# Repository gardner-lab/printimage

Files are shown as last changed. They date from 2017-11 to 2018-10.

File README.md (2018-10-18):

# Requirements

- [ScanImage](http://scanimage.vidriotechnologies.com/)  by Vidrio Technologies.
  - Version ≥5.2.4 ([Requirements](http://scanimage.vidriotechnologies.com/display/SIH/ScanImage+Installation+Instructions))
  - Other versions, including the nonfree versions, may also work, but are untested.
  - PrintImage requires that these pieces of hardware be configured in ScanImage:
    - Resonant scanner
    - Fast Z piezo stage
    - Pockels cell controlled by a fast analogue output card
    - Pockels power calibration hardware (e.g. a photodiode)
    - For stitched printing: an XYZ stage with around 0.1% linear error
- Mesh Voxelisation by Adam H. Aitkenhead: [Matlab File Exchange 27390](https://www.mathworks.com/matlabcentral/fileexchange/27390-mesh-voxelisation)
- STL File Reader by Eric Johnson: [Matlab File Exchange 22409](https://www.mathworks.com/matlabcentral/fileexchange/22409-stl-file-reader)
- Significant Figures by Teck Por Lim: [Matlab File Exchange 10669](https://www.mathworks.com/matlabcentral/fileexchange/10669-significant-figures)

# Installation

- Install ScanImage in the MATLAB path
- Run ScanImage and set up your hardware
- Calibrate hardware
  - Lens safe working depth
  - Lens FOV
  - Resonant scanner degrees per volt
  - Galvo degrees per volt
  - Slow XY or XYZ stage accuracy
  - Fast Z stage accuracy
- Patch the ScanImage code. In a shell, go to your ScanImage base directory, and run something like `git apply ../printimage/scanimage-integration/patches/scanimage-5.3.1.patch --whitespace=fix` (here I've assumed that scanimage and printimage are subdirectories of a common parent). If you don't see your favourite ScanImage version here, look at the patch: it's dead simple!
  - [For ScanImage 5.2.4](scanimage_integration/patches/scanimage-5.2.4.patch)
  - [For ScanImage 5.3](scanimage_integration/patches/scanimage-5.3.patch)
  - [For ScanImage 5.3.1](scanimage_integration/patches/scanimage-5.3.1.patch)
  - [For ScanImage 5.4](scanimage_integration/patches/scanimage-5.4.patch)
- Install PrintImage and the above packages in the MATLAB path
- Modify the appropriate PrintImage default parameters (this will be in a configuration file eventually)

# Calibration

Size Calibration is done through parameters in ScanImage's `Machine_Data_File.m`, not through PrintImage. This is because we figure you'll want your microscope calibrated properly whether or not you're printing anything today.

I will refer to the axis over which the resonant scanner scans as X. The galvo scans over Y. The "fast Z" stage, perpendicular to the focal plane, is (surprise!) Z.

Unsurprisingly, you will want to set zoom to 1, using either ScanImage's interface or `hSI.hRoiManager.scanZoomFactor = 1`

For X and Y, three parameters affect two degrees of freedom. I think there's a correct way to do this, but I'll describe the kludge.

## X and Y (field of view)

### Background

ScanImage mainains its idea of the lens's field of view in a variable called `hSI.hRoiManager.imagingFovUm`. This is a matrix giving the corner positions of the FOV. I've assumed that this is square and centered around 0, so if it's not, my code will be buggy! But here's one way to read ScanImage's idea of the FOV in X and Y:

        fov = hSI.hRoiManager.imagingFovUm
        [fov(3,1) - fov(1,1)      fov(3,2) - fov(1,2)]

### Parameters in `Machine_Data_File.m`

- `objectiveResolution` controls X and Y FOV together
- `rScanVoltsPerOpticalDegree` controls the magnitude of the voltage signal to the resonant scanner (X)
- `galvoVoltsPerOpticalDegreeY` controls the magnitude of the voltage signal to the galvo (Y)

### Setting the values

You'll need a way to measure the actual FOV. This can be done by imaging something of known size, or by printing something and then measuring it on a calibrated device. For this purpose we have calibration rulers. <em>FIXME Add links to our calibration rulers and the paper's instructions.</em>

This accomplished, compute your error in X and Y, and just multiply some combination of those numbers to scale the image. It is likely that the numbers have nominal values (e.g. for our hardware, in theory `galvoVoltsPerOpticalDegreeY = 1`), so maybe try not to stray too far from those values, or keep one of them at the nominal value or something. We've found that one iteration of this procedure can get us to within 1% or so.

### Scan phase

If the size of objects appears different on the left vs. right sides of the display (e.g. if you print or image a grid, and scrolling left-right changes the apparent grid size), you may need to adjust the scan phase. It's `hSI.hScan2D.linePhase`, available in the "Scan Phase" box in ScanImage's CONFIGURATION window. I haven't had much luck with "Auto Adjust".

Note that since this is not available in `Machine_Data_File.m`, I set it by hand in `printimage.m`. This will be moved to a printimage config file soon... For now, change the value until it looks right, and then modify `hSI.hScan2D.linePhase` in `printimage.m`.

## Z scale (adjusting the FastZ actuator)

### Background

ScanImage allows you to specify certain known models of FastZ stage. From `Machine_Data_File.m`:

        actuators(1).controllerType = 'thorlabs.pfm450';           % If supplied, one of {'pi.e665', 'pi.e816', 'npoint.lc40x', 'analog'}.

We have a ThorLabs pfm450, which ScanImage <em>should</em> know how to talk to. However, ours was not moving quite as far as ScanImage expected. In order to correct that, I modified some variables.

Also, note that it is essential to run at least our FastZ controller in closed-loop mode!

### Measuring the error

The procedure is generally the same as for X and Y: either print something of ostensible size and measure it, or image something of known size. For this we provide a vertical pyramid ruler. <em>FIXME Link to it!</em>

### Setting the values

If you need to adjust the scaling, you must <em>not</em> tell ScanImage what kind of FastZ controller you have, so it will actually use your adjusted values rather than its own. Just tell it you're using an analog controller:

        actuators(1).controllerType = 'analog';          % If supplied, one of {'thorlabs.pfm450', 'pi.e665', 'pi.e816', 'npoint.lc40x', 'analog'}.

Now, adjust the VoltsPerMicron values according to your measurements:

        actuators(1).commandVoltsPerMicron = (10/450)/1.1;    % Conversion factor for desired command position in um to output voltage

The maximum voltage is 10 (specified in the manual, transcribed to `actuators(1).maxCommandVolts`; likewise the 450 and other constants (see below).

<em>The "/1.1" is the important part--it compensates for the 10% error that we measured.</em>

        actuators(1).commandVoltsOffset = [];        % Offset in volts for desired command position in um to output voltage
        actuators(1).sensorVoltsPerMicron = (10/450)/1.1;     % Conversion factor from sensor signal voltage to actuator position in um. Leave empty for automatic calibration

Same thing here--the sensor was off by the same amount. That led us to double-check our measurements (looks like two independent (?) systems were in agreement), but the printed parts really were the wrong size, measured on an SEM and via our slow Z stage (Sutter MOM, which is notoriously inaccurate but which in this case agreed with the SEM, as well as with itself at different locations in its range). So that can happen, I guess. Photoresist shrinkage? Anyway, our parts are the right size now.

        actuators(1).sensorVoltsOffset = -0.12;        % Sensor signal voltage offset. Leave empty for automatic calibration
        actuators(1).maxCommandVolts = 10;          % Maximum allowable voltage command
        actuators(1).maxCommandPosn = 450;           % Maximum allowable position command in microns
        actuators(1).minCommandVolts = 0;          % Minimum allowable voltage command
        actuators(1).minCommandPosn = 0;           % Minimum allowable position command in microns

## Leveling (with a hexapod)

### Background:

Desiderata:
- We want the slide (or printable medium) to be parallel with the optical plane.
- We want moves to track the optical plane.

Now imagine that your printable medium is a piece of something (e.g. an electrode in need of a cuff) loosely taped onto a slide. It may not be parallel to, well, anything. First step is to tilt the medium into alignment with the optical plane. Second step is to align the movement coordinate system.

### Tilting

Start a "focus", and add a bullseye. Focus on the substrate, and then bring the lens up just far enough to see a hint of fluorescence beginning to show. Use the hexapod's angle controls to put that hint of fluorescence in the middle of the FOV (using the bullseye). It will probably be necessary to tilt the object and then re-focus on the hint-of-fluorescence, tilt some more, re-focus again, etc.

### Leveling

Again focus on the substrate and then bring the lens up just far enough to see a hint of fluorescence, as above. Run a "brightness test" and look at the results (FIXME `falloff_slide.m` right now, but that's not ready for primetime). The goal will be to set the leveling coordinate system so that the (possibly tilted, but optically aligned) substrate moves along the optical XY plane. This is controlled by 
  `STL.motors.hex.leveling = [ X Y Z U V W ];`
Set it in `printimage_config.m`, and adjust as needed. For example, on our printer:
- If brightness increases as X increases, increase V (pos 5)
- If brightness increases as Y increases, increase U (pos 4)
Your printer may differ.

My favourite workflow: edit the values in `printimage_config.m`, copy and paste the definition into the MATLAB commandline, and run `hexapod_set_leveling()`, which will store the values in the hexapod. Run another brightness test and repeat until the brightness traces don't change too much over XY movement (I can usually get them down to about 10% variation, depending on how close I am to the substrate).

The sixth value of `STL.motors.hex.leveling` controls the alignment of stitched parts. Print something stitched and adjust W in order to align the hexapod's XY motion with the resonant-galvo axis.

### Saving the tilt

One more parameter should be saved in `printimage_config.m`:
  `STL.motors.hex.slide_level = [ 0 0 0 0.255 -0.09 0 ];`
These numbers are the tilt offsets from the tilt calibration process, above, but they must be read _after_ the leveling coordinate system is correctly defined and tuned.

## Vignetting compensation

### Background

This began as an effort to model the falloff due to optical vignetting. The theoretical model of cos(theta)^4 seemed to fit pretty well, but couldn't be justified for a near-field laser (i.e. working less than a few kilometres from the laser source). And then I reasoned that since all models are wrong, it might be better to do something free-form. Hence the adaptive power compensation.

### THINGS I NEED TO FIX

- This requires a stitching stage with good precision, and currently actually requires the Physik-Instrumente hexapod controller! Sorry... I'll see about fixing that, or helping someone with other hardware to write a patch.
- I need to figure out at what size and zoom to print the test object!

### How?

Zero: Set your desired print zoom level...? Still working on this.

First, focus within the IP-Dip (yielding a fluorescent image that appears approximately Gaussian). Use `Calibrate / Save baseline image` to save the default brightness at the camera.

Second, find the substrate: follow the instructions regarding "Finding 0" in "Printing" (below in this document), and use the `Calibrate / Calibrate vignetting compensation` menu item to begin. This will:
- Load and print a "cube" (actually a rectangular prism) of the size defined at the top of `calibrate_vignetting_slide.m`.
- Servo the stitching stage over the printed cube near its surface (currently `height - 2` um) and measure the brightness at lots of points
- Fit a curve to the measured brightnesses
All future prints will use this curve to adjust the power in real time as objects print. If the curve isn't producing good results, you may do the same thing again (start with "Finding 0" again), which will print another cube using the curve you just generated, measure output, and create a new fit, _which will be stacked on top of the old one._ In this way, you may iterate until you get good results (I've only tried up to 5 iterations; there is no software limit but I have found that I get diminishing returns or even degradation of results after about 2. YMMV).

To start from scratch, use the `Calibrate / Clear vignetting compensation` menu item. You may then start again. Feel free to add your own calibration procedure! They're applied in `printimage_modify_beam.m`.

# Printing

## Preparing the sample

- Undeveloped IP-Dip is _extremely_ toxic. Use gloves, and treat all spills, wipes, etc., as biohazard waste.
- Place a drop of IP-Dip on the substrate.
  - We use a syringe or a stirring rod to place the IP-Dip.
  - For a test substrate, we use a microscope slide cover slip suspended by its ends. This ensures that if the lens is lowered too far, the cover slip will break before anything expensive.

## Interacting with the substrate

The working distance of the lens is important, as you do not want the lens to touch anything solid! Our lens has a 380-um working distance, which has the following implications:
- If we are focused on the surface of the substrate we can move down another 380 microns before something breaks.
  - If we have just printed something 200 um high, we can scroll down 180 um before the lens hits the thing we just printed.
- If we are imaging at substrate+10 um and moving the XY stage, anything over 390 um (previously printed, or slide holders, etc) can potentially hit the lens.

### Finding 0 (where the substrate meets the IP-Dip)

- Lower the lens until it touches the IP-Dip.
- Set ScanImage's zoom level to 1.
- Set ScanImage's power level somewhere too low to cause polymerisation. This will take experience, but start at 5%. On our equipment, at zoom level 1, polymerisation does not happen below around 40%, so we image at 10% or so.
- Press the ScanImage "FOCUS" button to begin obtaining images.
  - ScanImage's view window should glow, and you will probably see some vignetting at zoom=1.
- IP-Dip fluoresces at the print wavelength (780 nm), and glass does not. As long as the lens is focusing in the IP-Dip, the microscope will show an image. Lower the lens until the whole FOV turns dark, indicating that the lens is now focused on the substrate. Lowering another micron or 3 ensures good bonding.

### Printing in a specific location (e.g. on a nonuniform object attached to the substrate)
- Align according to your best guess.
- Find an appropriate lens depth (Z).
- Search outward from there using the "Search" button until the object you want to print on appears in the image.
- If you must manually rotate the sample, it is helpful to tell PrintImage about the axis of rotation:
  - Find the centre of your rotation stage by imaging something (possibly something you just printed) and rotating the stage, servoing until the centre of rotation is in the centre of the ScanImage imaging window.
  - Press the PrintImage "Set rotation centre" button.
    - You may also want to change the PrintImage parameter STL.logistics.rotation_centre to match this.
  - From now on, if you manually rotate the stage, you can have PrintImage track the location of the object by entering the angle of rotation in the "Track rotation" box.
- The "Print preview" button will paint the current preview slice (PrintImage's rightmost figure) where PrintImage will print it. You can then move the item under the image to align it.
  - But it's not quite accurate: it shows where PrintImage will turn up the power to the Pockels, but does not take into account any delays in the latter's response.

## Power calibration

PrintImage's "Power Test" button will print a bunch of rectangular prisms at various power settings, which can be seen in ScanImage's "Power Box Settings" window, available through the "POWER CONTROLS" window.
- Unfortunately there is a nonlinear relationship between zoom level, Z step size, and polymerisation power required. If those parameters change, you should re-run the power test at that level.
- Set the "Print Power" level to something that polymerises but doesn't bubble.

## Understage zeroing

### Aligning a rotation stage with the microscope stage

Print something (e.g. a power test pattern). Use the rotation slider to rotate the stage, and see if it rotates about the centre of the screen (the "bullseye" can be used to facilitate this). Move the microscope stage toward what looks like the centre of rotation. Repeat until the image rotates about the centre of the field. This is the alignment point. You may add "STL.motors.mom.understage_centre = [12655 10857 16890];" to  your printimage_config, reading those numbers off the microscope stage's location (microns).

### Leveling a hexapod

Find the substrate, and then pull the lens just a little bit away from it so you can just see some light in the image centre. Scroll up and down on Y while adjusting the hexapod's X rotation control such that scrolling on Y doesn't affect the spot's brightness (closeness to substrate). Vice versa for X-Y.

For Z, print something that involves stitching, such as a linearity test. Scrolling back and forth with the microscope's stage should produce motion parallel with the line of dots that the stitching procedure produced.

The final numbers can be added to printimage_config; e.g., "STL.motors.hex.leveling = [0 0 0 0.9 -0.1 -1.1];"

## Controlling print dimensions

- Your system probably has the worst resolution along the resonant scanner's axis, which we call X. If the object to be printed has finer features along one dimension than another, use PrintImage's dimension buttons to choose to place the coarser features along X
- Objects are printed in slices from Z=0 to higher Z. Slices that print later must attach to slices that print earlier. The Z axis should have no overhangs.
  - Because PrintImage is so fast, we have noticed that some overhangs are okay: the overhanging part may not have time to drift away. But this is untested: do not rely on it! Rather, choose Z so that there are no overhangs.

## Controlling print resolution

X and Y resolutions are functions of various things (position on the X axis, zoom level, hardware...), and you have limited control over them. Z is easiest.

- X "resolution" is always determined by the speed of the analogue output card controlling your Pockels cell. It will always be as high as it can be. There's no single number for this--voxels are smaller near the edges of the FOV than in the middle where the resonant scanner moves the beam faster. Sorry.
- Y resolution is controlled by the number of Y scan lines: ScanImage's `Lines / Frame` parameter in the CONFIGURATION window, also available at the command line through `hSI.hRoiManager.linesPerFrame`. It is always a power of two, so the choice of actual resolutions is somewhat limited. Resolution is the FOV / number of scan lines. Useful resolutions are determined by your photoresist, optics, etc.
- Z resolution is agnostic to zoom level, and it's measured in real units. Woot! Please control this through PrintImage's variable `STL.print.zstep`, which is in microns, and it will instruct ScanImage correctly <em>assuming ScanImage moves your FastZ stage in the same direction as mine with the same voltage change. You may need to change the sign and do a little minor debugging.</em> (Internally, PrintImage controls ScanImage's internal variable `Steps/Slice` in the FAST Z CONTROLS window (`hSI.hStackManager.stackZStepSize`).) One version of the PrintImage interface gives you direct control over that, but if you don't see it, then you have to modify the variable in `printimage.m`.

## Controlling print size

Because STL files are dimensionless, you have to choose the size of the object.

### Stitching

If the object to be printed exceeds any of the dimensions allowed by your hardware, PrintImage will break it into parts and print them in sequence using your XYZ stage.
- Z and safe-working-depth warning!

# After printing

## Inspecting the print

## Resetting the Z position

## Developing the print

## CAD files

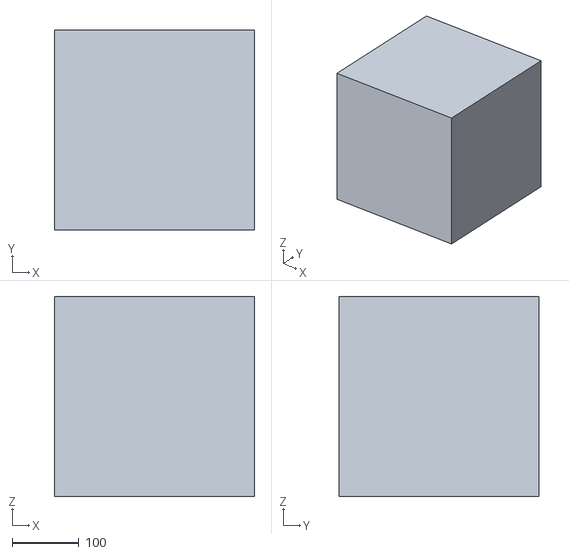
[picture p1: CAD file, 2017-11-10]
STL files/cube.stl
300.0 x 300.0 x 300.0

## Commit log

2016-11-09 Initial GUI: read an STL, display slices, sweep through them, allow choice of print Z axis. Basically, display management.
2016-11-17 GUI to control printing!
    Reads an STL file, allows visually scanning through it with a scrollbar.
    Allows choice of print axis.
    Allows control of print power.
    DOES NOT handle scaling/aspect ratio/etc yet...
2016-11-17 Allow either printing or just normal imaging: use print power only from PRINT button.
2016-11-17 Ask for desired size, and print at the correct size!
2016-11-18 Fix scaling. It was screwing up the aspect ratio.
    Fix problem in which the updated scanpath was not being saved.
    Decrease power (appropriately?) when zoomed in.
    Add some debugging code...
2016-11-22 Change fig to cross-platform--compatible units.
    Don't squash printed object (keep Z at end-of-print value rather than
    resetting to 0).
2016-11-23 Voxelisation / slice viewer now shows the actual print-resolution slices if possible (i.e. ScanImage has computed the X resolution), not some fantasy.
    Also, I've added some code to try to run a scan (ask ScanImage to compute
    X resolution on demand) but it didn't work. Yet?
2016-11-29 (1) "Power Calibration" button prints cubes at 25 different powers.
    (2) Print in the correct order (low--high) without TimO's
    piezo-control-reversing box.
    (3) Various attempts to prevent the lens from squashing its creation. They
    all failed.
2016-11-29 Allow switching between printing and power test.
    Add "linear" vs "log" power tests.
    Fix units on fig.
2016-12-01 More options:
    - Boolean flag for whether or not TimO's fastZ-reverser is in place.
    - Boolean flag for whether to invert slice order
    - Double the number of patches in the power test: now 5x10.
    - Lower FastZ to 450 (should take this number from hSI, but 450 for now)
2016-12-13 Control print dims for all axes. Also finish merge to printimage.fig.
2016-12-15 Change Resonant and Galvo volts per optical degree in a bid to fix aspect ratio.
2016-12-19 Random:
    - Change default power test to "linear"
    - Scale power when zoomed (doesn't work right, but better now)
    - Re-voxelise when needed, not all the time.
2017-01-04 New Motors section; still doesn't work.
    Found bug: changed FastZ config from "analog" to "thorlabs.pfm450". Seems
    control is now better: the "actual" motor position tracks "desired" much
    better now.
2017-01-12 Sutter MPC-200 motor stage integrated.
    Beam control (Pockels) integrated.
2017-01-18 Add control for which beam to print on.
2017-02-01 Store the object inside unit cube, but rescale to actual desired dimensions for voxelisation and printing.
    New control for minimum good zoom (presumably that which eliminates vignetting, or can be used as a kludge to control resolution.
2017-02-02 MAJOR AND UNTESTED: Add ability to print large objects using the slow stage.
    - Object is now represented in microns rather than in a unit cube.
    - Voxel positions are computed in microns given the ostensible FOV.
    - Each metavoxel is computed separately, and then printing iterates over them.
    - To Do: compute STL.print.metavoxel_shift[x,y,z]; put a call to the real motor command in printimage; figure out how to make hSI.startLoop() block until finished.
2017-02-06 Add needed things from last checkin; add control over print metavoxel size.
2017-02-07 Current status: fails to produce an ao_volts_raw.B of the correct size.
    Further bugfixes.
2017-02-07 Printing works again for single metavoxels...
    Zoom factor management.
    Bugfixes.
2017-02-07 Invert works correctly now. Printing upside down should pose no difficulties.
    More motor stage bugfixes.
2017-02-08 Fix bug #12 (add waitbar for print and voxelise)
    Fix bug #9 (changing print zoom controls now forces revoxelisation)
    Fix bug #8 (More "go back to origin" buttons)
    Fix bug #7 (Do not cut off bottom of print when bottom is empty)
2017-02-09 Add "abort" button, although it may not work.
    Try to manage re-voxelisation a bit better (untested).
    Add debugging info to try to understand weird print geometry.
2017-02-13 Motor stage is aligned. Printing stitched objects, but getting weird rectangles extending wherever the right edge of the Beam is nonzero. Fix flyback blanking!
2017-02-17 Ok handling of empty slices.
    Show slices in orientation corresponding to print (axis ij).
2017-02-17 Various:
    - Set hSI.hScan2D.linePhase manually in opening function.
    - Fix buggy metavoxel computation.
    - Update slice preview as each metavoxel is being printed.
    - Startup: don't slew to [0 0 0], but back off 450um with slow Z stage and
    then drop fastZ (should do this according to actual pos of fastZ).
    - Restore zoom factor after UpdateBounds.
    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
2017-02-22 Add functionality: re-voxelise for print, test motor stage...
2017-02-27 Position stage test now randomises block print order.
2017-03-03 Printimage's waitbar now shows ETA.
2017-03-04 Add ability to change aspect ratio of printed part. KLUDGE...
2017-03-06 Cancel button works now, for voxelising and printing.
2017-03-28 PRINT PREVIEW!
    Untested. Probably doesn't really work quite right just yet.
2017-03-29 Show actual Z slice pos for calibration.
    Misc. bugfixes.
2017-03-29 Show autozoom setting (necessary for power tests!)
2017-03-30 Several:
    - Compensate (maybe? At least the code) for ThorLabs FastZ calibration
    fail.
    - Move waitbars out of the way.
    - Allow image-stack saves during print.
    - Remove some debugging prints.
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2017-04-17 Revert "Power compensation for sinusoidal speed"
    This reverts commit 68021924cd0f4930eceefd4ddc3f9d68619c734d.
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2017-04-19 Bugfix in printimage.m
2017-04-19 Christos fixes a bug in beam sinusoidal power compensation
2017-04-19 Christos fixes a bug in sinusoid power compensation
2017-04-19 Fix issues #22 (search around current point) and #23 (track stage rotation).
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2017-05-02 Fix bugs #15 and #26!
    Machine_Data_File:
    - #15: Calibration for ThorLabs pfm450! (Have to run it in analogue mode, not
    pfm450 mode). Must manually turn on Closed Loop on the control box.
    - #26: Reintroduce forgotten calibrated value for degreesPerVolt for resonant scanner.
    - Increase Sutter ROE-200 timeout for long moves
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2017-05-25 NEW code for virtual rotation points:
    - Alignment code (incl. bullseye) for calibrating MOM -- PI positioning
    - Set height for PI virtual rotation centre
    - All computations look ok
    - PI code appears to ignore the newly set virtual rotation centre, so this
    is FAIL
2017-05-25 Motor stage rotation:
    - More useful failure mode when range is exceeded.
    - Ad-hoc calibration of motor stage virtual rotation point. Seems to be
    scaled wrong, or not to work for values that aren't big enough, or
    something??
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2017-05-31 (1) Switch to KSD-style coordinate system transforms so I can reset the centre of rotation even if the frame is rotated. This does not seem to work yet; support request sent.
    (2) Make sure hexapod is at [0 0 0] at initialisation (safely?!) and
    before and after printing and linearity-testing. This will throw an error
    because it's untested and possibly dangerous.
2017-06-02 Linearity test now prints a cube all the way on the RHS of the FOV. This reduces beam speed and therefore random errors...?
2017-06-08 Fix Galvo volts/degree so parts come out closer to the right size. Also 2-d scale bar.
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2017-08-09 Fix code for rotation stage, at least. Startup and rotation control are tested.
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2017-08-09 FIXED an unlisted bug in which rotation immediately followed by print led to the wrong motions.
2017-09-25 Various changes for new hexapod: - new IP address - faster motions work, so use them! - manually controlled motions should be fast. - Remove up-down of MOM when un-rotating hexapod (???) - Fix hexapo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
2017-10-24 Remove all parameters from cos4 fit. This seems to print pretty well. Doesn't require a "fit" toolbox, but I'm leaving a dummy optimisation var to keep it general and easy to play with.
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2017-10-31 Printimage now automates the error-prone aspects of energy deposition analysis.
2017-11-07 BUGFIX: save/restore hexapod position in the same units :}
    Misc changes to behaviour of power test and stuff.
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2017-11-09 Various: - tools for showing power adjustments due to beam speed and vignetting - bugfixes from previous checkin - offline mode now knows enough to do beam power compensation - offline mode looks bet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
2017-11-10 New controls: level the slide (shouldn't this be folded into "zero rotation"?), control height of slide measurement.
    [polyimide test cube.STL]
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2017-12-06 Vignetting compensation is almost fully automated at the single-iteration level.
    [cube.stl]
2017-12-12 First poly2, then poly4. Compute #frames correctly!
2017-12-12 When measuring brightness, correctly compute the number of frames to acquire.
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
